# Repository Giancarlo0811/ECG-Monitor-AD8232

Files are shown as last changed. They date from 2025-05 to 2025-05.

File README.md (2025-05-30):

# ECG-Monitor-AD8232
Diseño de Monitor ECG (Electrocardiograma) de una sola derivación (Single Lead) basado en el AFE TI AD8232.

## 📚 Proyecto Académico
*Proyecto desarrollado como parte de la asignatura ***EC3083 Taller de Equipos Electrónicos*** en la Universidad Simón Bolívar.*

**Objetivo**: Diseñar un circuito ECG con esquemático y PCB layout.

## 🛠️ Detalles Técnicos
- **Herramientas**:
    - **Proteus**: Esquemático, simulación y PCB.
    - **KiCad**: Esquemático y PCB.
- **Características clave**:
    - **Analog Front End (AFE)**: TI AD8232.
    - **Acondicionamiento de señal**: filtro pasabanda 0.445-43.6 Hz (simulado en Proteus).
    - **Ganancia media banda**: 59.1 dB (simulado en Proteus).
    - **Diseño PCB**: 2-layer layout.
    - **Bill of Materials (BOM)**: Lista de componentes completa con costos.

## 📸 Esquemático + PCB

### Proteus
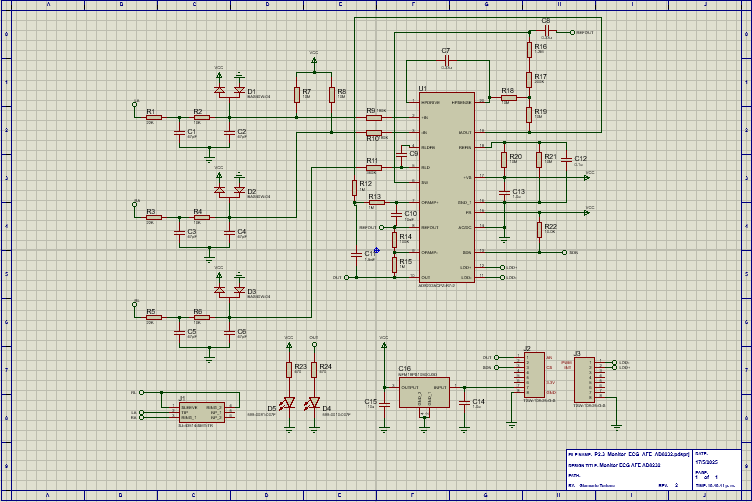
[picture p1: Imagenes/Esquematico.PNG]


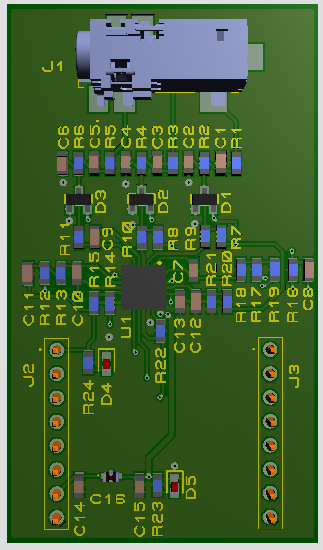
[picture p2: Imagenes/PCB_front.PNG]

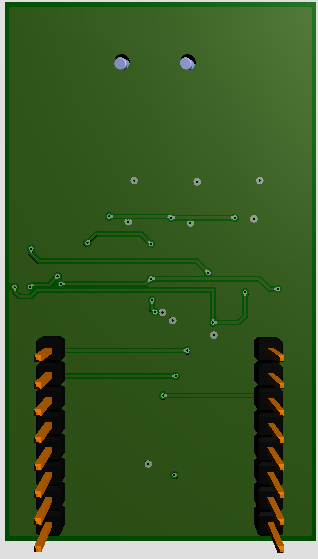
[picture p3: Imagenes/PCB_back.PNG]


### KiCad
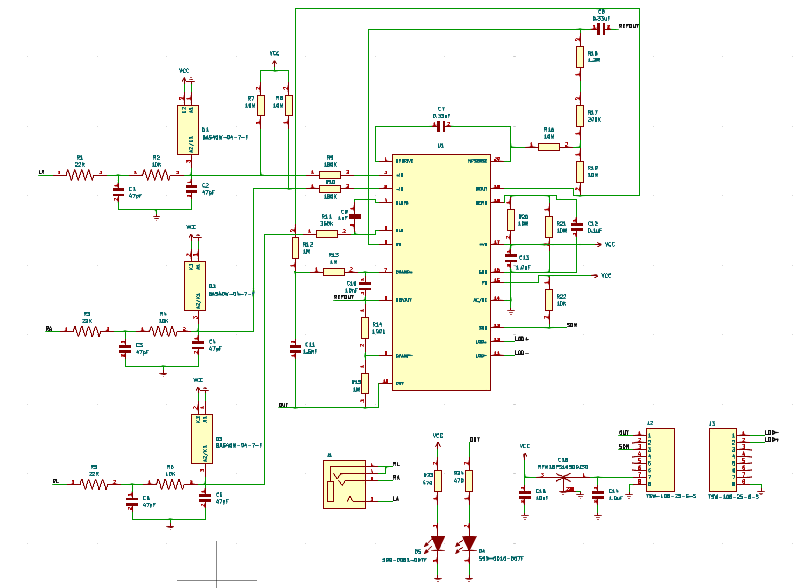
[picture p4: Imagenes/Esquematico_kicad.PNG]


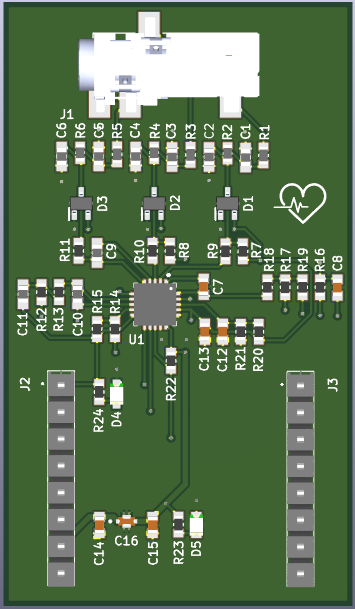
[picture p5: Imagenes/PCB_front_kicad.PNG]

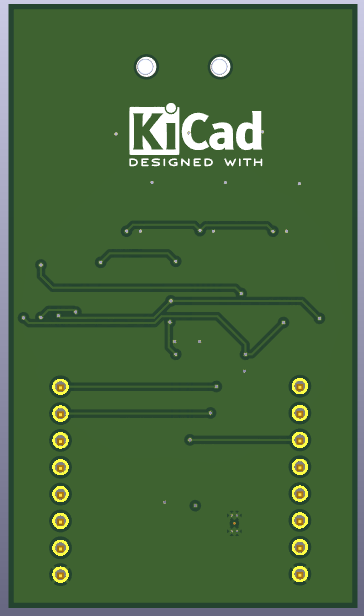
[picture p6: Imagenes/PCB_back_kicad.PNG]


## 📊 Simulación
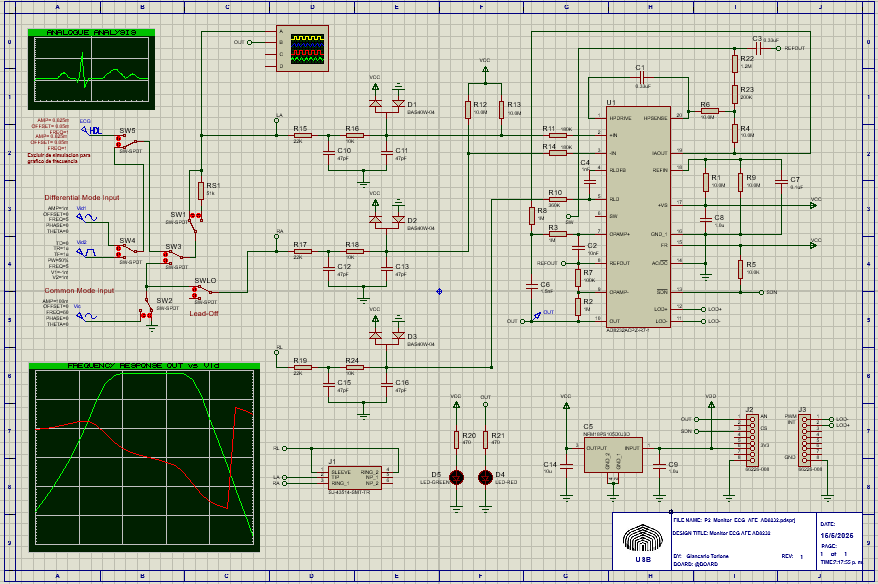
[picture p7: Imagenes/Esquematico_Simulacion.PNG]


### 📈 Bode de amplitud y fase de la ganancia modo diferencial
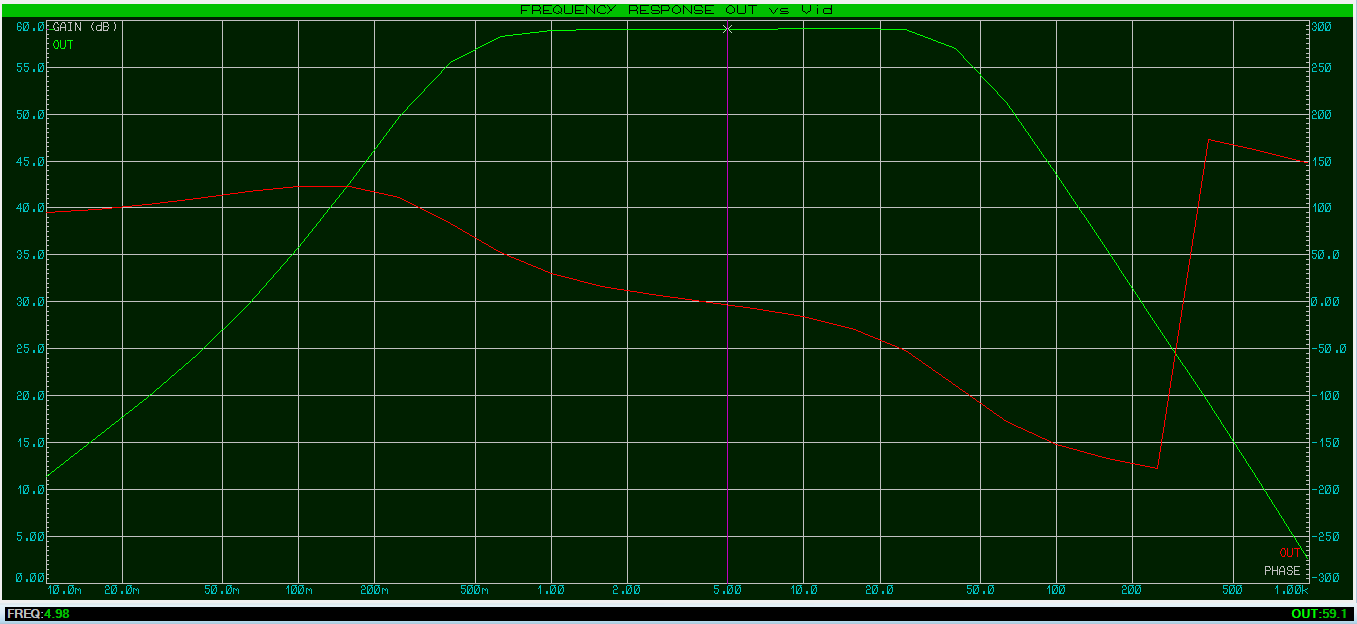
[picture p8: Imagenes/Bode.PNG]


Caso pasa bajo: fc = 43.6 Hz

Caso pasa alto: fc = 0.445 Hz

Avd = 59,1 dB frecuencias medias

### 📈 Vid (ECG simulado 0.625 mVp) y Vo (OUT)
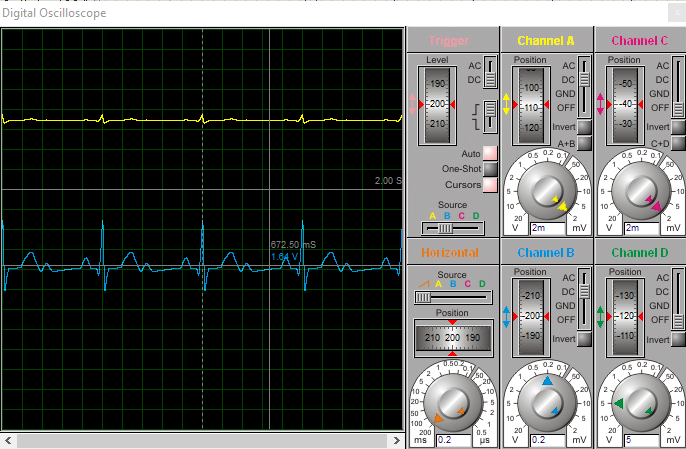
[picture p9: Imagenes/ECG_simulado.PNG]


## 📋 BOM (Bill of Materials)
[Descargar BOM](./Documentos/BOM_Monitor_ECG_AFE_AD8232.xlsx)

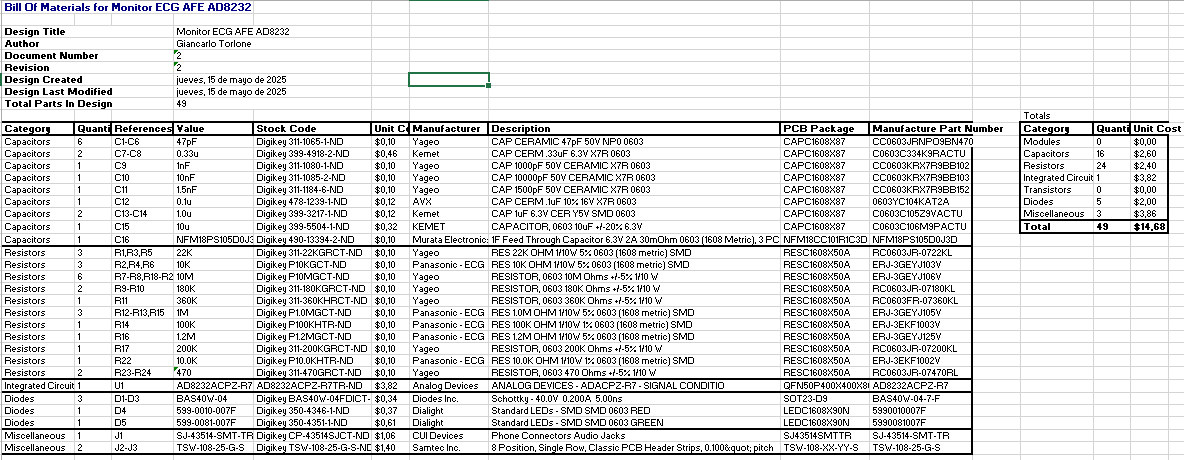
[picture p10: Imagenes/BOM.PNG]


## 📂 Documentación completa
Para una documentación más detallada descargar:
[Presentación PDF](/Documentos/Presentacion_ECG_Monitor_AFE_AD8232.pdf)

## ⚠️ Disclaimer
Esto es un diseño teórico. La fabricación de la PCB y sus pruebas están pendientes.

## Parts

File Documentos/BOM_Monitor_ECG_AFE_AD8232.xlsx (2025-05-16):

Bill Of Materials for Monitor ECG AFE AD8232
Design Title |  |  | Monitor ECG AFE AD8232
Author |  |  | Giancarlo Torlone
Document Number |  |  | 2
Revision |  |  | 2
Design Created |  |  | jueves, 15 de mayo de 2025
Design Last Modified |  |  | jueves, 15 de mayo de 2025
Total Parts In Design |  |  | 49
 |  |  |  |  |  |  |  |  |  | Totals
Category | Quantity | References | Value | Stock Code | Unit Cost | Manufacturer | Description | PCB Package | Manufacture Part Number | Category | Quantity | Unit Cost
Capacitors | 6 | C1-C6 | 47pF | Digikey 311-1065-1-ND | $0,10 | Yageo | CAP CERAMIC 47pF 50V NP0 0603 | CAPC1608X87 | CC0603JRNPO9BN470 | Modules | 0 | $0,00
Capacitors | 2 | C7-C8 | 0.33u | Digikey 399-4918-2-ND | $0,46 | Kemet | CAP CERM .33uF 6.3V X7R 0603 | CAPC1608X87 | C0603C334K9RACTU | Capacitors | 16 | $2,60
Capacitors | 1 | C9 | 1nF | Digikey 311-1080-1-ND | $0,10 | Yageo | CAP 1000pF 50V CERAMIC X7R 0603 | CAPC1608X87 | CC0603KRX7R9BB102 | Resistors | 24 | $2,40
Capacitors | 1 | C10 | 10nF | Digikey 311-1085-2-ND | $0,10 | Yageo | CAP 10000pF 50V CERAMIC X7R 0603 | CAPC1608X87 | CC0603KRX7R9BB103 | Integrated Circuits | 1 | $3,82
Capacitors | 1 | C11 | 1.5nF | Digikey 311-1184-6-ND | $0,10 | Yageo | CAP 1500pF 50V CERAMIC X7R 0603 | CAPC1608X87 | CC0603KRX7R9BB152 | Transistors | 0 | $0,00
Capacitors | 1 | C12 | 0.1u | Digikey 478-1239-1-ND | $0,12 | AVX | CAP CERM .1uF 10% 16V X7R 0603 | CAPC1608X87 | 0603YC104KAT2A | Diodes | 5 | $2,00
Capacitors | 2 | C13-C14 | 1.0u | Digikey 399-3217-1-ND | $0,12 | Kemet | CAP 1uF 6.3V CER Y5V SMD 0603 | CAPC1608X87 | C0603C105Z9VACTU | Miscellaneous | 3 | $3,86
Capacitors | 1 | C15 | 10u | Digikey 399-5504-1-ND | $0,32 | KEMET | CAPACITOR, 0603 10uF +/-20% 6.3V | CAPC1608X87 | C0603C106M9PACTU | Total | 49 | $14,68
Capacitors | 1 | C16 | NFM18PS105D0J3D | Digikey 490-13394-2-ND | $0,10 | Murata Electronics | 1F Feed Through Capacitor 6.3V 2A 30mOhm 0603 (1608 Metric), 3 PC Pad | NFM18CC101R1C3D | NFM18PS105D0J3D
Resistors | 3 | R1,R3,R5 | 22K | Digikey 311-22KGRCT-ND | $0,10 | Yageo | RES 22K OHM 1/10W 5% 0603 (1608 metric) SMD | RESC1608X50A | RC0603JR-0722KL
Resistors | 3 | R2,R4,R6 | 10K | Digikey P10KGCT-ND | $0,10 | Panasonic - ECG | RES 10K OHM 1/10W 5% 0603 (1608 metric) SMD | RESC1608X50A | ERJ-3GEYJ103V
Resistors | 6 | R7-R8,R18-R21 | 10M | Digikey P10MGCT-ND | $0,10 | Yageo | RESISTOR, 0603 10M Ohms +/-5% 1/10 W | RESC1608X50A | ERJ-3GEYJ106V
Resistors | 2 | R9-R10 | 180K | Digikey 311-180KGRCT-ND | $0,10 | Yageo | RESISTOR, 0603 180K Ohms +/-5% 1/10 W | RESC1608X50A | RC0603JR-07180KL
Resistors | 1 | R11 | 360K | Digikey 311-360KHRCT-ND | $0,10 | Yageo | RESISTOR, 0603 360K Ohms +/-5% 1/10 W | RESC1608X50A | RC0603FR-07360KL
Resistors | 3 | R12-R13,R15 | 1M | Digikey P1.0MGCT-ND | $0,10 | Panasonic - ECG | RES 1.0M OHM 1/10W 5% 0603 (1608 metric) SMD | RESC1608X50A | ERJ-3GEYJ105V
Resistors | 1 | R14 | 100K | Digikey P100KHTR-ND | $0,10 | Panasonic - ECG | RES 100K OHM 1/10W 1% 0603 (1608 metric) SMD | RESC1608X50A | ERJ-3EKF1003V
Resistors | 1 | R16 | 1.2M | Digikey P1.2MGCT-ND | $0,10 | Panasonic - ECG | RES 1.2M OHM 1/10W 5% 0603 (1608 metric) SMD | RESC1608X50A | ERJ-3GEYJ125V
Resistors | 1 | R17 | 200K | Digikey 311-200KGRCT-ND | $0,10 | Yageo | RESISTOR, 0603 200K Ohms +/-5% 1/10 W | RESC1608X50A | RC0603JR-07200KL
Resistors | 1 | R22 | 10.0K | Digikey P10.0KHTR-ND | $0,10 | Panasonic - ECG | RES 10.0K OHM 1/10W 1% 0603 (1608 metric) SMD | RESC1608X50A | ERJ-3EKF1002V
Resistors | 2 | R23-R24 | 470 | Digikey 311-470GRCT-ND | $0,10 | Yageo | RESISTOR, 0603 470 Ohms +/-5% 1/10 W | RESC1608X50A | RC0603JR-07470RL
Integrated Circuits | 1 | U1 | AD8232ACPZ-R7-2 | AD8232ACPZ-R7TR-ND | $3,82 | Analog Devices | ANALOG DEVICES - ADACPZ-R7 - SIGNAL CONDITIO | QFN50P400X400X80-21 | AD8232ACPZ-R7
Diodes | 3 | D1-D3 | BAS40W-04 | Digikey BAS40W-04FDICT-ND | $0,34 | Diodes Inc. | Schottky - 40.0V 0.200A 5.00ns | SOT23-D9 | BAS40W-04-7-F
Diodes | 1 | D4 | 599-0010-007F | Digikey 350-4346-1-ND | $0,37 | Dialight | Standard LEDs - SMD SMD 0603 RED | LEDC1608X90N | 5990010007F
Diodes | 1 | D5 | 599-0081-007F | Digikey 350-4351-1-ND | $0,61 | Dialight | Standard LEDs - SMD SMD 0603 GREEN | LEDC1608X90N | 5990081007F
Miscellaneous | 1 | J1 | SJ-43514-SMT-TR | Digikey CP-43514SJCT-ND | $1,06 | CUI Devices | Phone Connectors Audio Jacks | SJ43514SMTTR | SJ-43514-SMT-TR
Miscellaneous | 2 | J2-J3 | TSW-108-25-G-S | Digikey TSW-108-25-G-S-ND | $1,40 | Samtec Inc. | 8 Position, Single Row, Classic PCB Header Strips, 0.100&quot; pitch | TSW-108-XX-YY-S | TSW-108-25-G-S

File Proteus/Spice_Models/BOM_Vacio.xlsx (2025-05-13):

Bill Of Materials for P8_Monitor_ECG_AFE_AD8232
Design Title |  |  | P8_Monitor_ECG_AFE_AD8232
Author
Document Number
Revision
Design Created |  |  | Monday, March 28, 2022
Design Last Modified |  |  | Monday, March 28, 2022
Total Parts In Design |  |  | 56
 |  |  |  |  |  |  |  |  |  | Totals
Category | Quantity | References | Value | Stock Code | Unit Cost | Manufacturer | Manufacture Part Number | Description | PCB Package | Category | Quantity | Unit Cost
Capacitors | 2 | C1,C3 | 0.33uF
Capacitors | 1 | C2 | 10nF
Capacitors | 1 | C4 | 1nF
Capacitors | 1 | C5 | NFM18PS105D0J3D
Capacitors | 1 | C6 | 1.5nF
Capacitors | 1 | C7 | 0.1uF
Capacitors | 2 | C8-C9 | 1.0u
Capacitors | 6 | C10-C13,C15-C16 | 47pF |  |  |  |  |  |  | Total
Capacitors | 1 | C14 | 10u
Resistors | 6 | R1,R4,R6,R9,R12-R13 | 10M
Resistors | 3 | R2-R3,R8 | 1M
Resistors | 1 | R5 | 10.0K
Resistors | 1 | R7 | 100K
Resistors | 1 | R10 | 360K
Resistors | 2 | R11,R14 | 180K
Resistors | 3 | R15,R17,R19 | 22K
Resistors | 3 | R16,R18,R24 | 10K
Resistors | 2 | R20-R21 | 470
Resistors | 1 | R22 | 1.2M
Resistors | 1 | R23 | 200K
Integrated Circuits | 1 | U1 | AD8232ACPZ-R7-2
Diodes | 3 | D1-D3 | BAS40W-04
Diodes | 1 | D4 | LED-RED
Diodes | 1 | D5 | LED-GREEN
Miscellaneous | 1 | J1 | SJ-43514-SMT-TR
Miscellaneous | 2 | J2-J3 | 66226-008
Miscellaneous | 1 | RS1 | 51k
Miscellaneous | 6 | SW1-SW5,SWLO | SW-SPDT

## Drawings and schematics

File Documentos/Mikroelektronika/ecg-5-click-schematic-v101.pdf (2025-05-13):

# ECG 5 click schematic v101

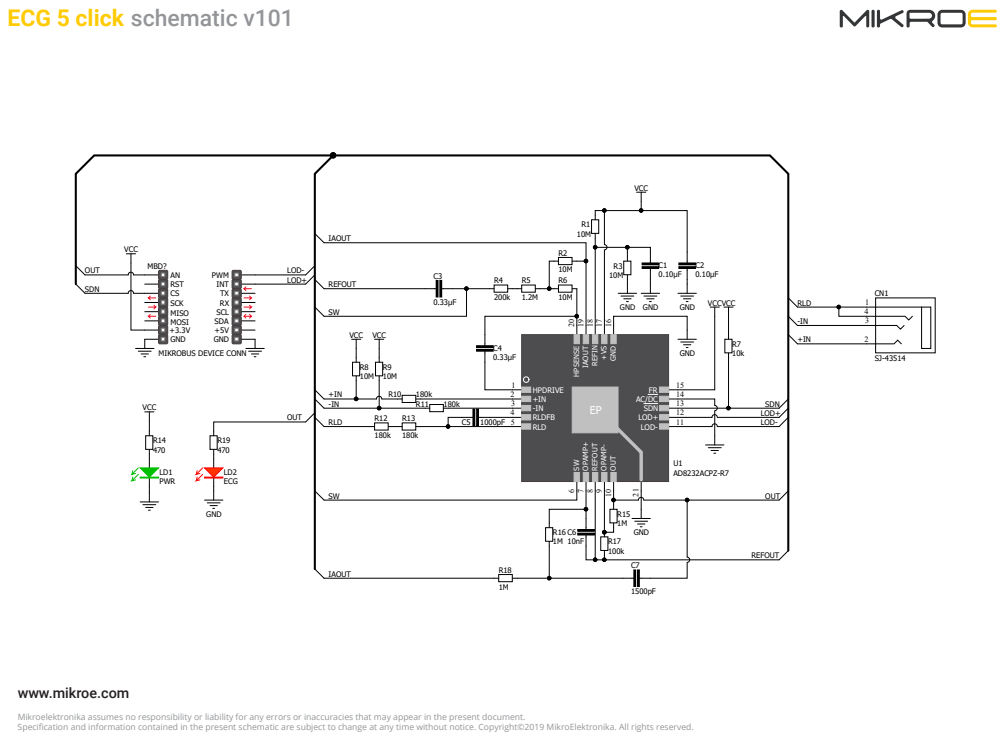
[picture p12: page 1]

GND 16 +VS 17 REFIN 18 IA

Mikroelektronika assumes no responsibility or liability for any errors or inaccuracies that may appear in the present document.
Specification and information contained in the present schematic are subject to change at any time without notice. Copyright©2019 MikroElektronika. All rights reserved.

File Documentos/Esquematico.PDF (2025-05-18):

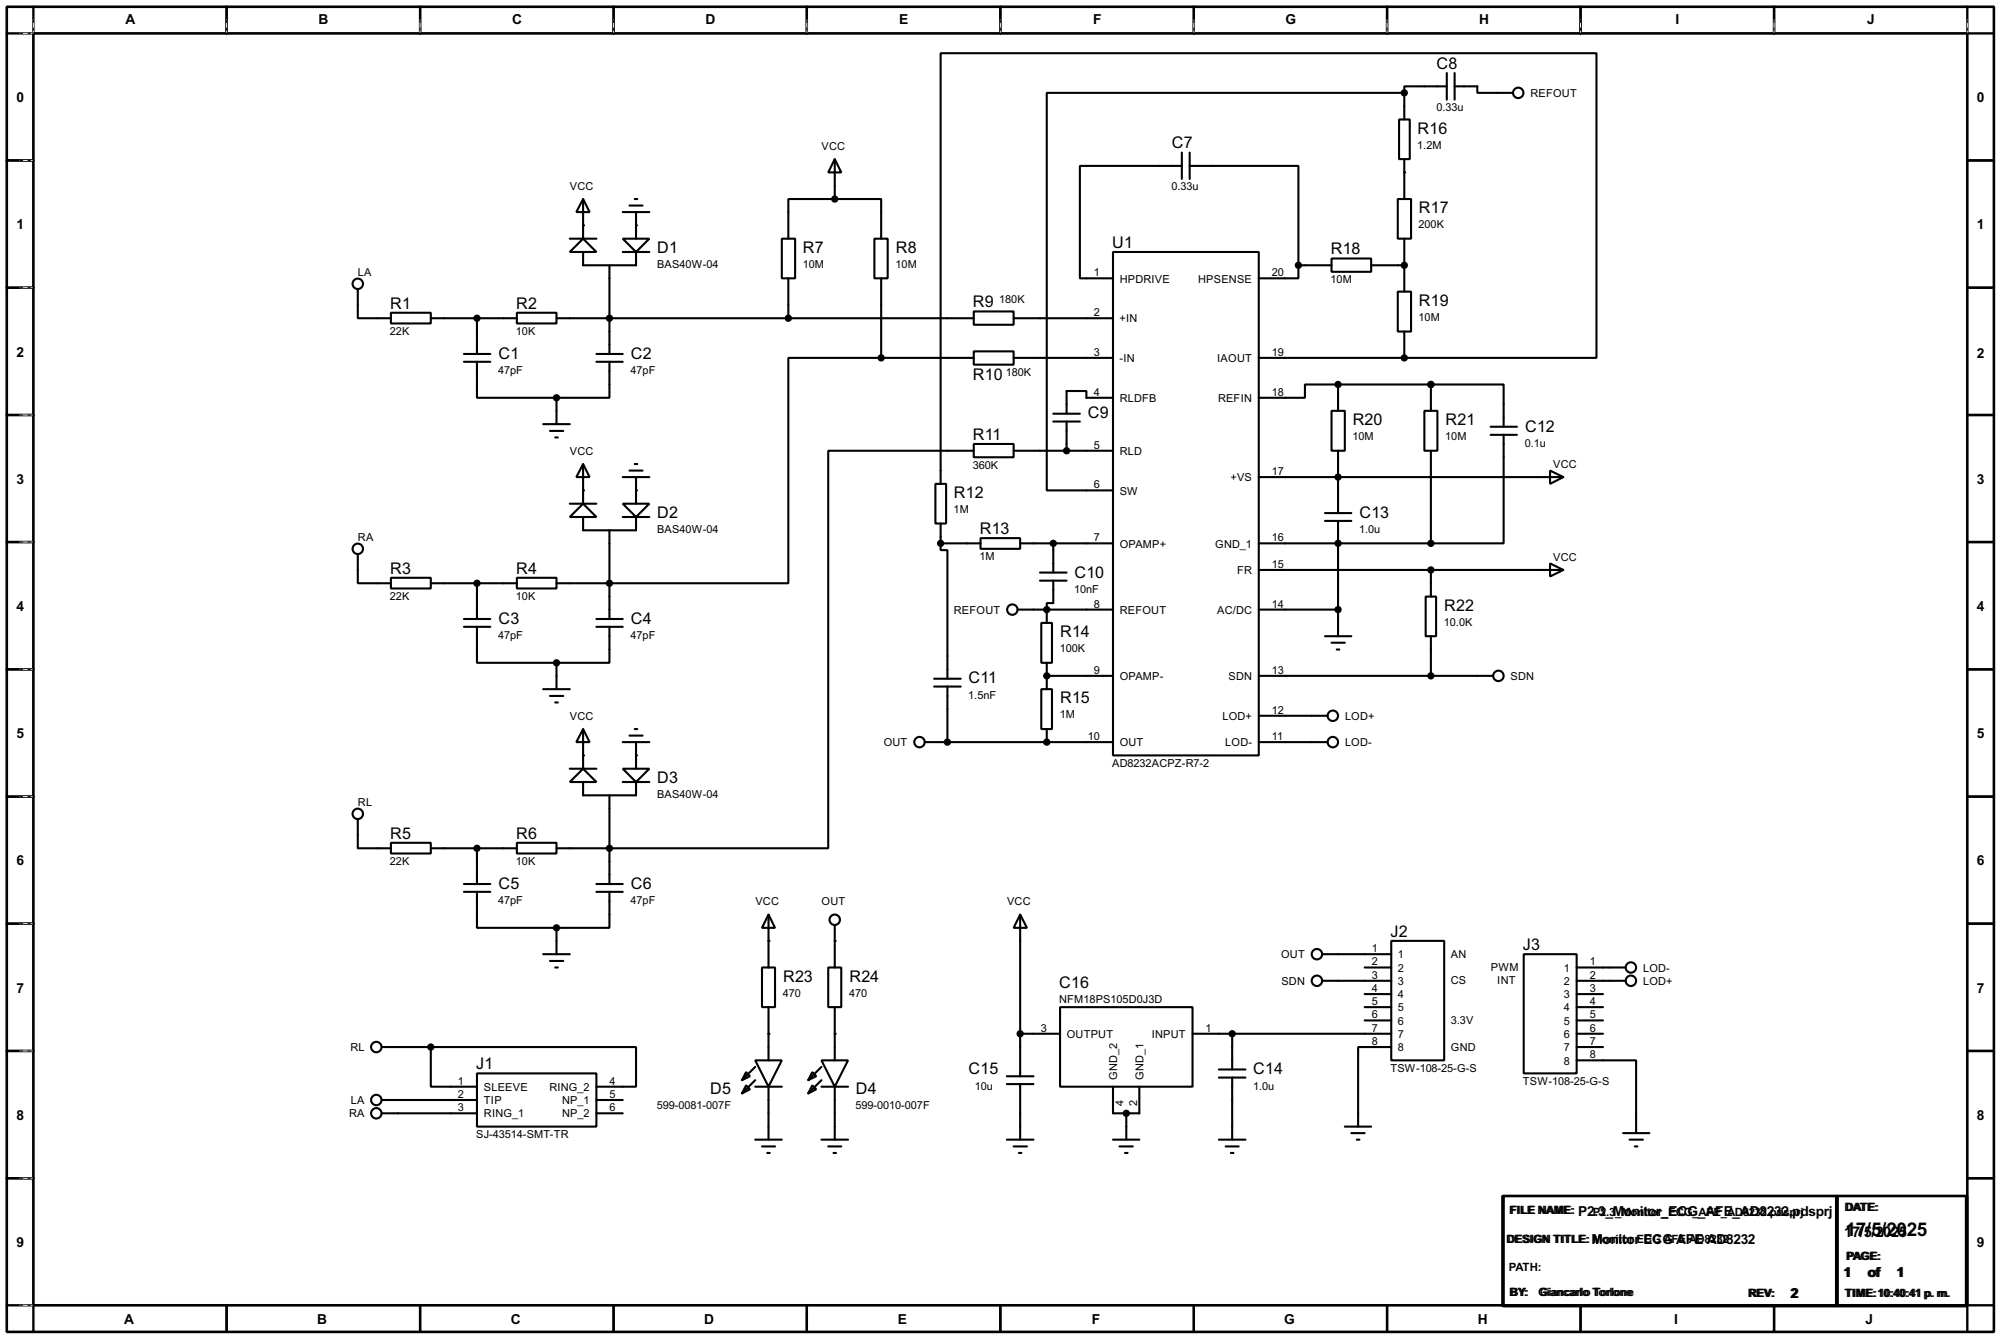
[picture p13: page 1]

SW OPAMP+ GND_1 FR REFOUT AC/DC SDN LOD+ OUT

LOD- LOD+ OUT SDN

DESIGN TITLE: Monitor ECG AFE AD8232

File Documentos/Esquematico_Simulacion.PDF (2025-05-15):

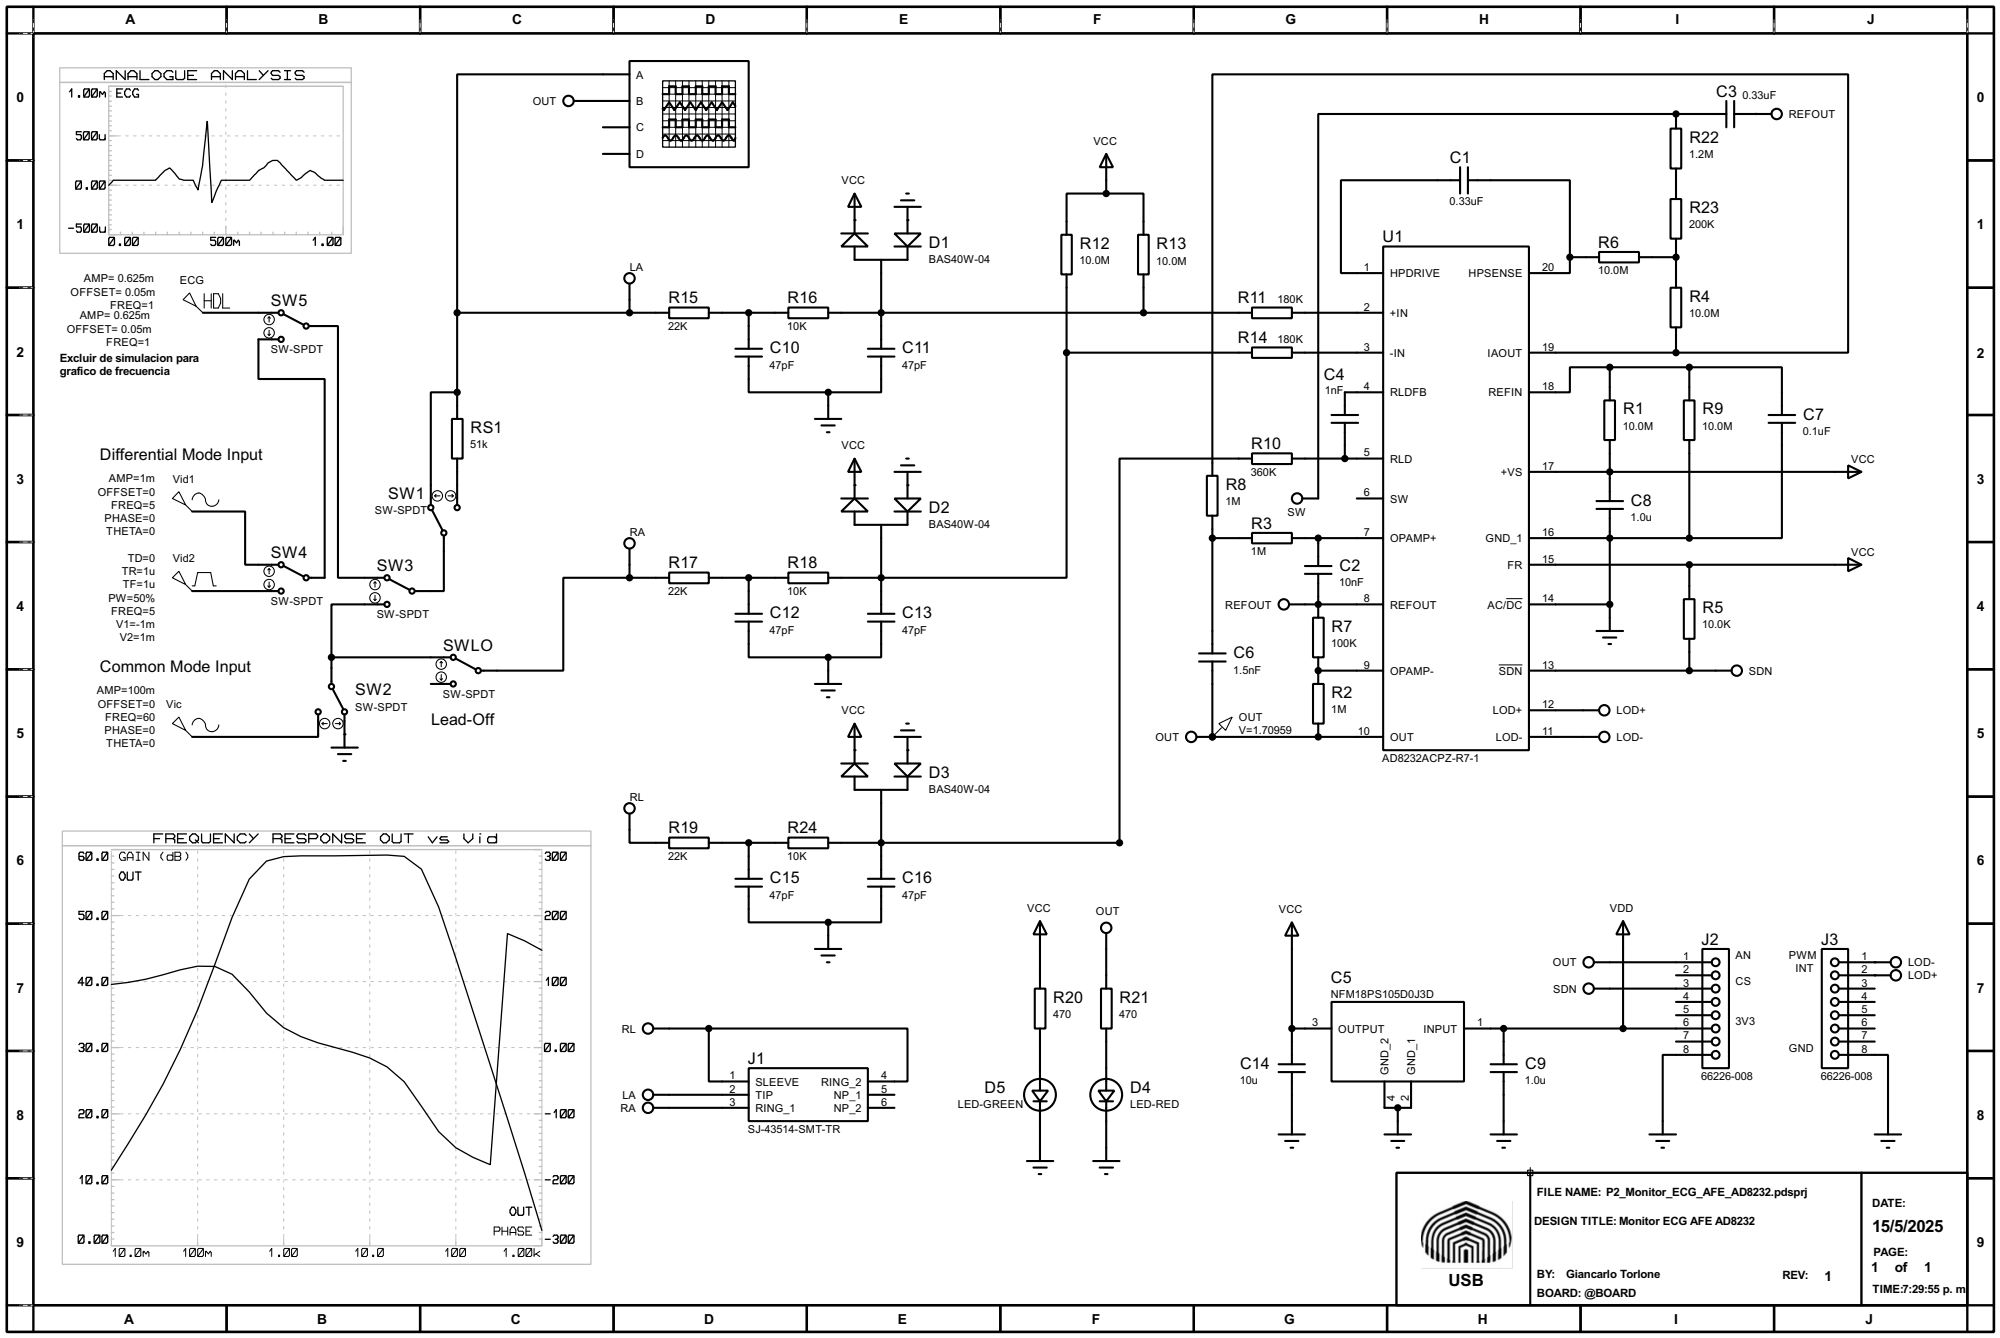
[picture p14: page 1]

Excluir de simulacion para grafico de frecuencia

Vic AMP=100m
OFFSET=0 FREQ=60 PHASE=0 THETA=0

SW-SPDT Lead-Off

LOD- LOD+ OUT SDN

DESIGN TITLE: Monitor ECG AFE AD8232

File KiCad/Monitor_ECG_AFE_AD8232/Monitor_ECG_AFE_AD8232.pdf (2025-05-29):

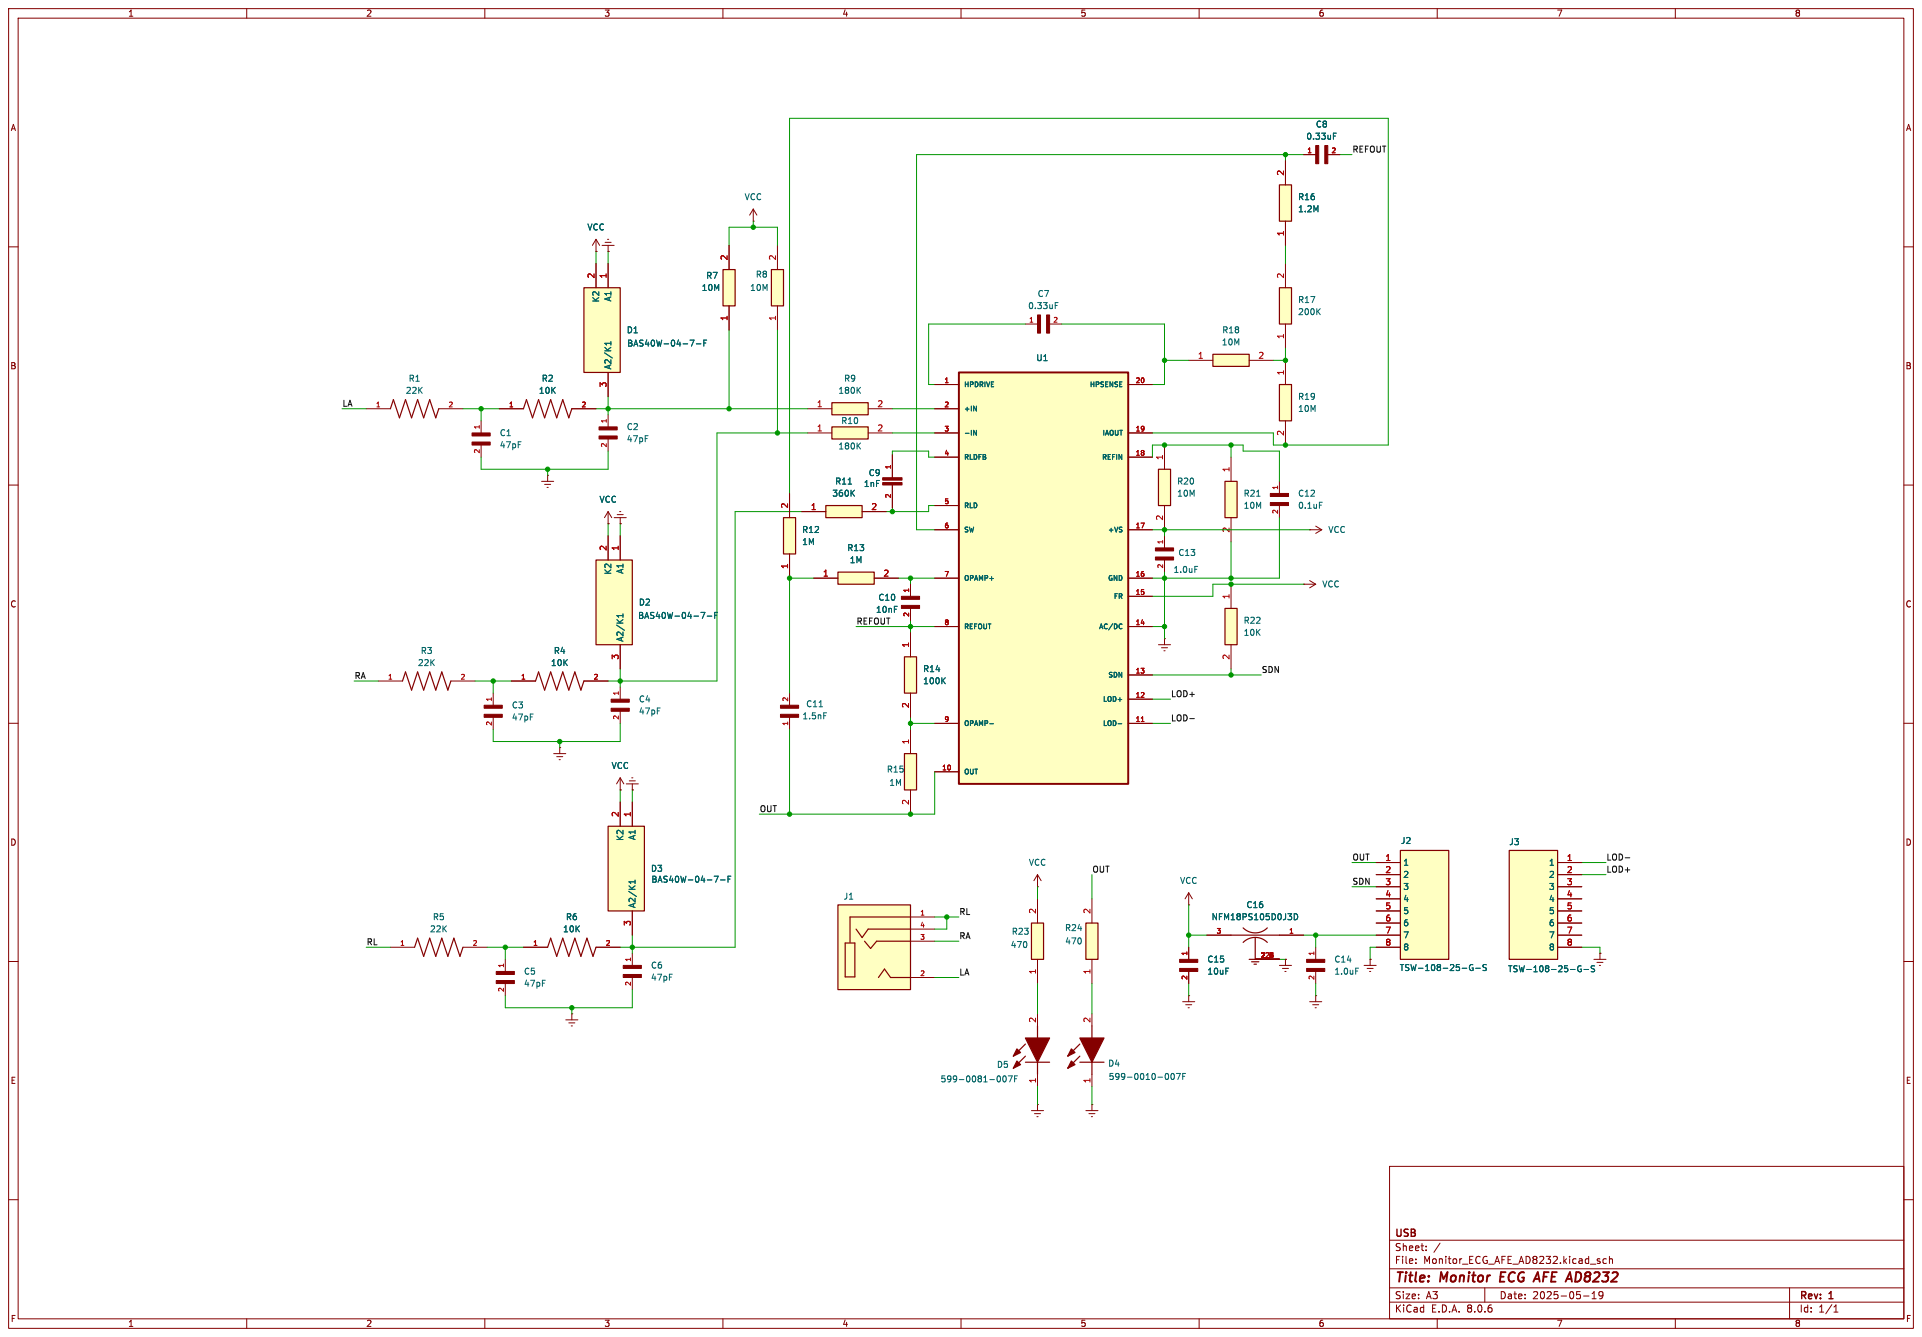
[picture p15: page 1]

Id: 1/1 Title: Monitor ECG AFE AD8232

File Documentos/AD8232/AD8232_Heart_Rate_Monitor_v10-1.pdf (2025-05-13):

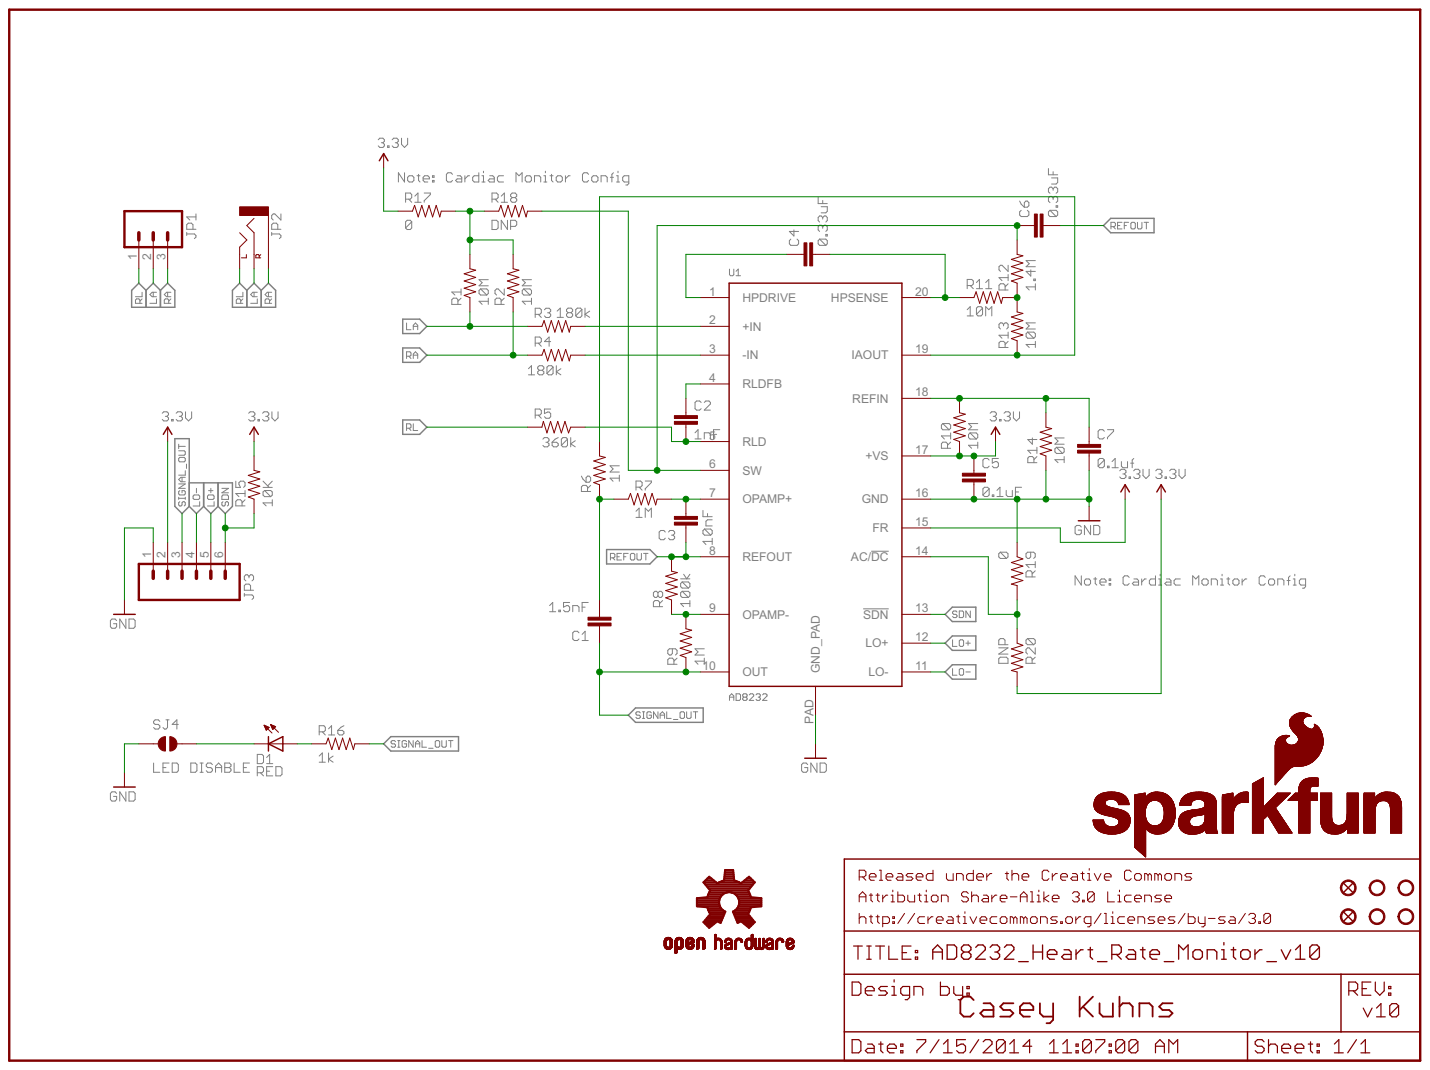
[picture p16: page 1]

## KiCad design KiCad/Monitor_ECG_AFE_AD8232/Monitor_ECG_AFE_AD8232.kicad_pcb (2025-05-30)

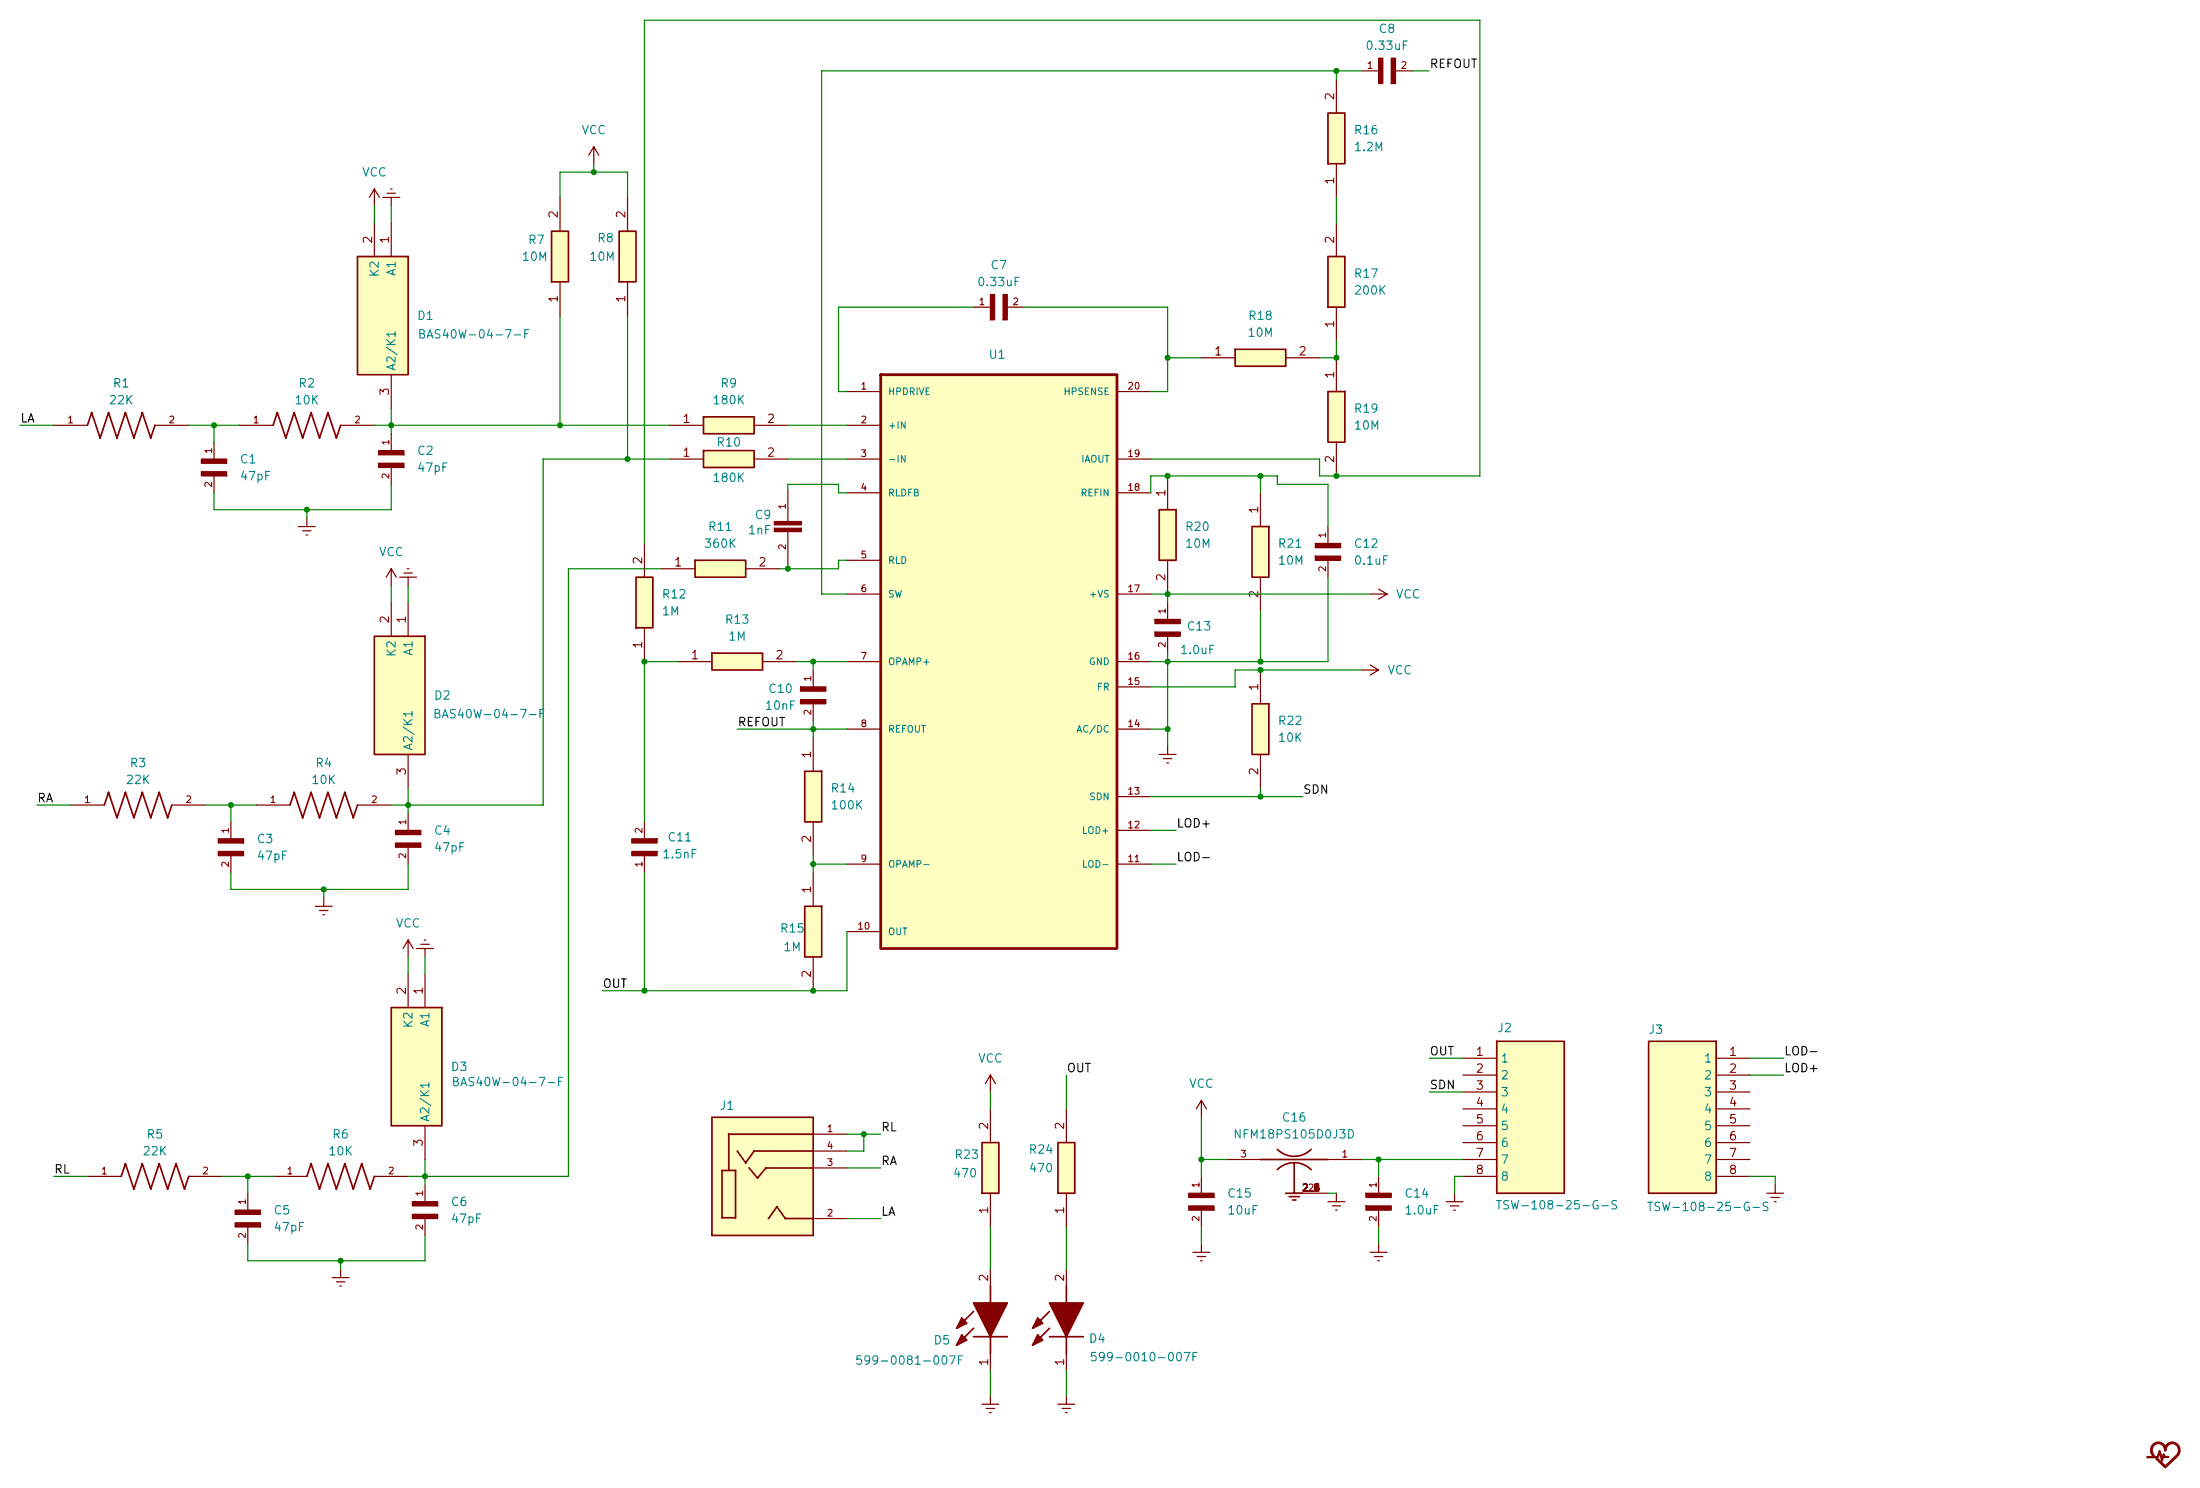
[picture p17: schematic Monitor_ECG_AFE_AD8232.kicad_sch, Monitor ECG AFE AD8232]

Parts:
C1, C2, C3, C4, C5, C6: 47pF; CAPC1608X90
C7, C8: 0.33uF; CAPC1608X87N
C9: 1nF; CAPC1608X90
C10: 10nF; CAPC1608X90
C11: 1.5nF; CAPC1608X90
C12: 0.1uF; CAPC1608X90N
C13, C14: 1.0uF; CAPC1608X90N
C15: 10uF; CAPC1608X90N
C16: NFM18PS105D0J3D; FIL_NFM18PS105D0J3D
D1, D2, D3: BAS40W-04-7-F; SOT65P222X110-3N; Manufacturer_Part_Number BAS40W-04-7-F; Mouser Part Number 621-BAS40W-04-F
D4: 599-0010-007F; LEDM168X70N; Manufacturer_Part_Number 599-0010-007F; Mouser Part Number 645-599-0010-007F
D5: 599-0081-007F; CAPC1608X95; Manufacturer_Part_Number 599-0081-007F; Mouser Part Number 645-599-0081-007F
ECG_logo1: LOGO; logo_5x5
J1: SJ-43514-SMT-TR; CUI_SJ-43514-SMT-TR; PARTREV 1.05
J2, J3: TSW-108-25-G-S; TSW-108-XX-YY-S; Manufacturer_Part_Number TSW-108-25-G-S; Mouser Part Number 200-TSW10825GS
R1, R3, R5: 22K; RESC1608X55N
R2, R4, R6: 10K; RES_ERJ-3GEYJ103V; PARTREV 3/1/2020
R7, R8, R18, R19, R20, R21: 10M; RESC1608X55N; Manufacturer_Part_Number ERJ-3GEYJ106V; Mouser Part Number 667-ERJ-3GEYJ106V
R9, R10: 180K; RESC1608X55N; Manufacturer_Part_Number RC0603JR-07180KL; Mouser Part Number 603-RC0603JR-07180KL
R11: 360K; RESC1608X55N; Manufacturer_Part_Number RC0603FR-07360KL; Mouser Part Number 603-RC0603FR-07360KL
R12, R13, R15: 1M; RESC1608X55N; Manufacturer_Part_Number ERJ-3GEYJ105V; Mouser Part Number 667-ERJ-3GEYJ105V
R14: 100K; RESC1608X55N; Manufacturer_Part_Number ERJ-3EKF1003V; Mouser Part Number 667-ERJ-3EKF1003V
R16: 1.2M; RESC1608X55N; Manufacturer_Part_Number ERJ-3GEYJ125V; Mouser Part Number 667-ERJ-3GEYJ125V
R17: 200K; RESC1608X55N; Manufacturer_Part_Number RC0603JR-07200KL; Mouser Part Number 603-RC0603JR-07200KL
R22: 10K; RESC1608X55N; Manufacturer_Part_Number ERJ-3EKF1002V; Mouser Part Number 667-ERJ-3EKF1002V
R23, R24: 470; RESC1608X55N; Manufacturer_Part_Number RC0603JR-07470RL; Mouser Part Number 603-RC0603JR-07470RL
U1: AD8232ACPZ-R7; QFN50P400X400X100-21N

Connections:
/LA: J1.2, R1.1
/LOD+: J3.2, U1.12 (LOD+)
/LOD-: J3.1, U1.11 (LOD-)
/OUT: C11.1, J2.1, R15.2, R24.2, U1.10 (OUT)
/RA: J1.3, R3.1
/REFOUT: C8.2, C10.2, R14.1, U1.8 (REFOUT)
/RL: J1.1, J1.4, R5.1
/SDN: J2.3, R22.2, U1.13 (SDN)
Earth: C1.2, C2.2, C3.2, C4.2, C5.2, C6.2, C12.2, C13.2, C14.2, C15.2, C16.2, C16.2_1, C16.2_2, C16.2_3, C16.2_4, C16.2_5, C16.2_6, D1.1 (A1), D2.1 (A1), D3.1 (A1), D4.1 (K), D5.1 (K), J2.8, J3.8, R21.2, U1.14 (AC/DC), U1.16 (GND)
unnamed: C1.1, R1.2, R2.1
unnamed: C3.1, R3.2, R4.1
unnamed: C5.1, R5.2, R6.1
unnamed: C11.2, R12.1, R13.1
unnamed: C14.1, C16.1, J2.7
unnamed: C2.1, D1.3 (A2/K1), R2.2, R7.1, R9.1
unnamed: C4.1, D2.3 (A2/K1), R4.2, R8.1, R10.1
unnamed: C6.1, D3.3 (A2/K1), R6.2, R11.1
unnamed: D4.2 (A), R24.1
unnamed: D5.2 (A), R23.1
unnamed: R16.1, R17.2
unnamed: R17.1, R18.2, R19.1
unnamed: R9.2, U1.2 (+IN)
unnamed: R10.2, U1.3 (-IN)
unnamed: C7.1, U1.1 (HPDRIVE)
unnamed: C7.2, R18.1, U1.20 (HPSENSE)
unnamed: R12.2, R19.2, U1.19 (IAOUT)
unnamed: C10.1, R13.2, U1.7 (OPAMP+)
unnamed: R14.2, R15.1, U1.9 (OPAMP-)
unnamed: C12.1, R20.1, R21.1, U1.18 (REFIN)
unnamed: C9.2, R11.2, U1.5 (RLD)
unnamed: C9.1, U1.4 (RLDFB)
unnamed: C8.1, R16.2, U1.6 (SW)
VCC: C13.1, C15.1, C16.3, D1.2 (K2), D2.2 (K2), D3.2 (K2), R7.2, R8.2, R20.2, R22.1, R23.2, U1.15 (FR), U1.17 (+VS)

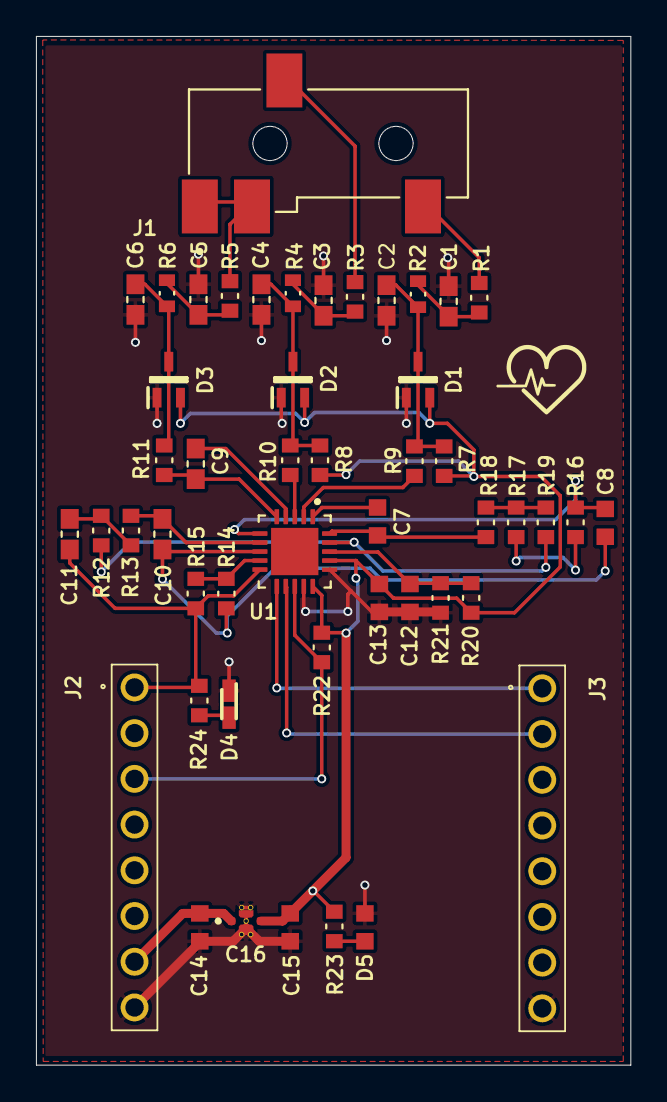
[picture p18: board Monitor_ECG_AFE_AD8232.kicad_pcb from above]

Board: 2 copper layers, 33.0 x 57.2 mm, 50 parts (0 on the bottom side), 33 nets.

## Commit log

2025-05-13 ECG monitor
    [BOM_Vacio.xlsx]
2025-05-16 readme actualizado
    [BOM_Monitor_ECG_AFE_AD8232.xlsx]
2025-05-18 proteus pcb y gerbers
2025-05-29 version KiCad agregada
    [0603YC104KAT2A.STEP, 5990081007F.STEP, 5990110007F.STEP, AD8232ACPZ-R7.step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]
2025-05-30 version kicad cambiada
    [Monitor_ECG_AFE_AD8232.kicad_pcb, Monitor_ECG_AFE_AD8232.kicad_sch]
2025-05-30 version kicad modificada
    [0603YC104KAT2A.STEP, 5990081007F.STEP, 5990110007F.STEP, AD8232ACPZ-R7.step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]
